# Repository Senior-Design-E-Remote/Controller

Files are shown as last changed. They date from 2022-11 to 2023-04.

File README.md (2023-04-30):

# E-Remote Quick Start Guide

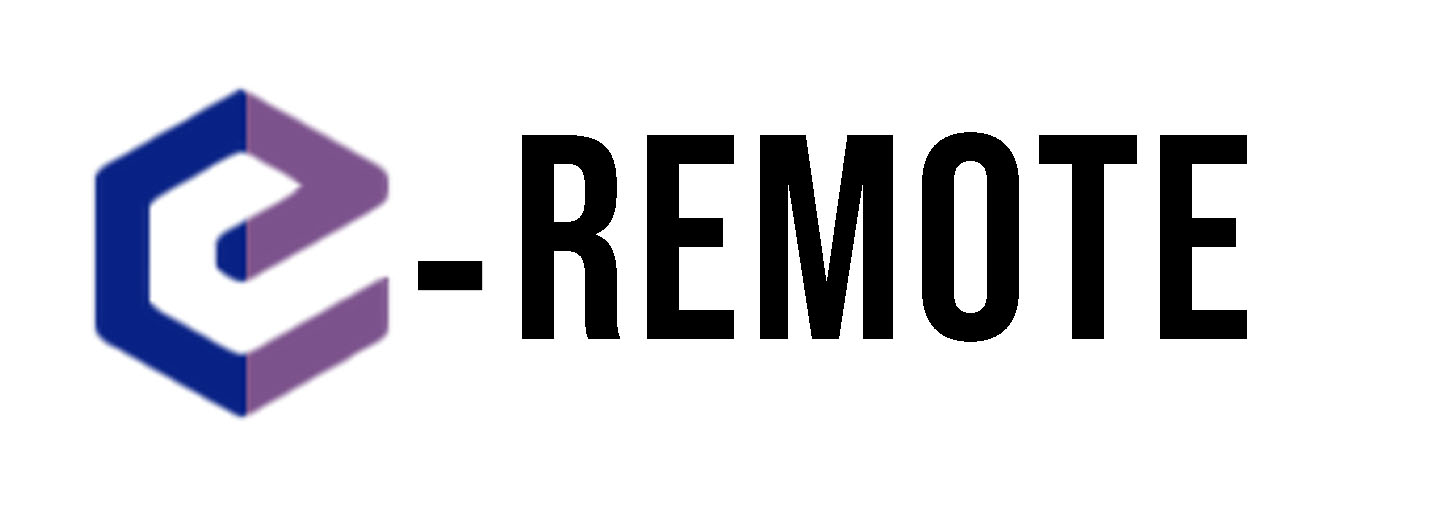
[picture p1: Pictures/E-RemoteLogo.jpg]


## Introduction and Current State

Welcome to E-Remote, an Inclusive Video Game Controller designed for people with hand arthritis. Our current product as seen below is a streamlined casing designed for maxmimm usability with minimal pain. Our finalized shell design is based on feedback from actual patients at Boston Medical Center, who's responses you can see reported in the Previous Reports folder.

Current Features include:
* Palm controlled joysticks
* Removable joystick caps with different size options available
* Touch capacitive buttons triggered by a tap
* A streamlined shell casing designed for wrist support while gaming
* Bluetooth Capabilities
* Battery and Micro USB power support
* Brightness adjustable color rotating LEDs

E-Remote is fully assembled and is currently able to connect to a Bluetooth capable computer and register itself as a generic gamepad. Once it is connected, you can open any game library that supports generic gamepads and play with minimal setup required (details for Steam can be found in the User Manual). 
On top of that, the WirelessController.ino code that powers E-Remote can also be ported to any Bluetooth capable ESP32 provided the Arduino IDE is properly setup, so you can build as many E-Remotes as you want.  

**Note**: The brightness adjusting logarithmic slider is directly connected to the 3.3V power and acts as a resistor for the LEDs to adjust their brightness. Brightness is not controlled by the code whatsoever.

### Final Product Setup

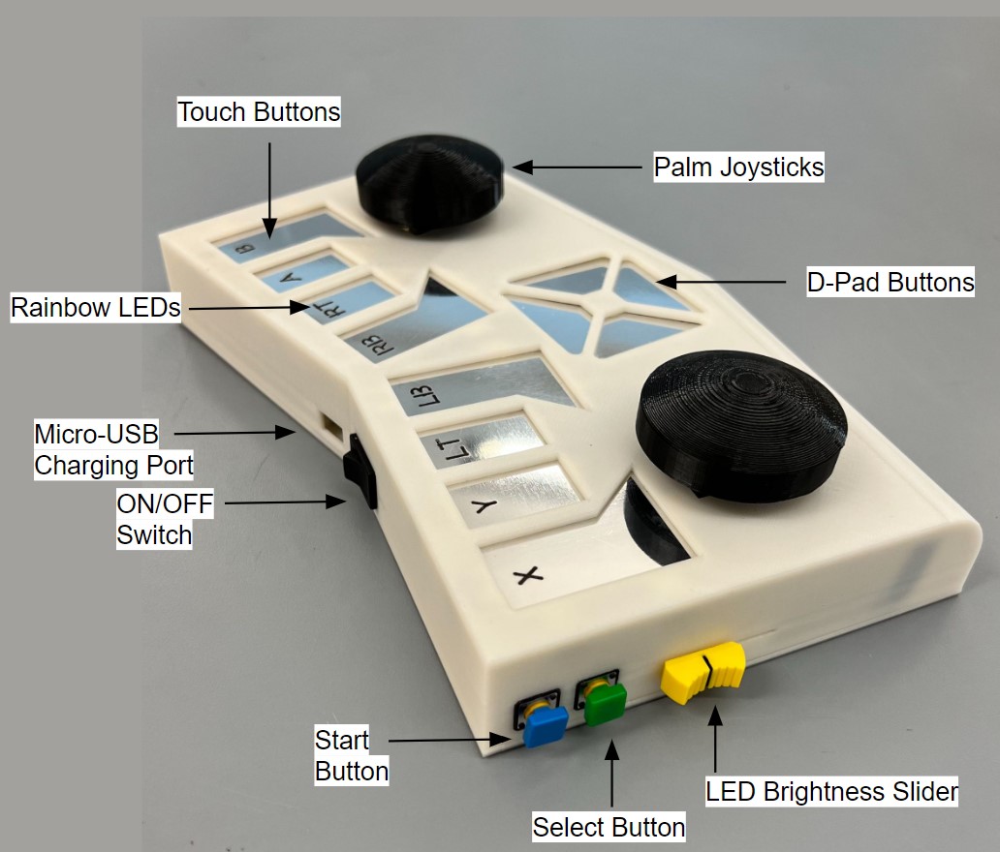
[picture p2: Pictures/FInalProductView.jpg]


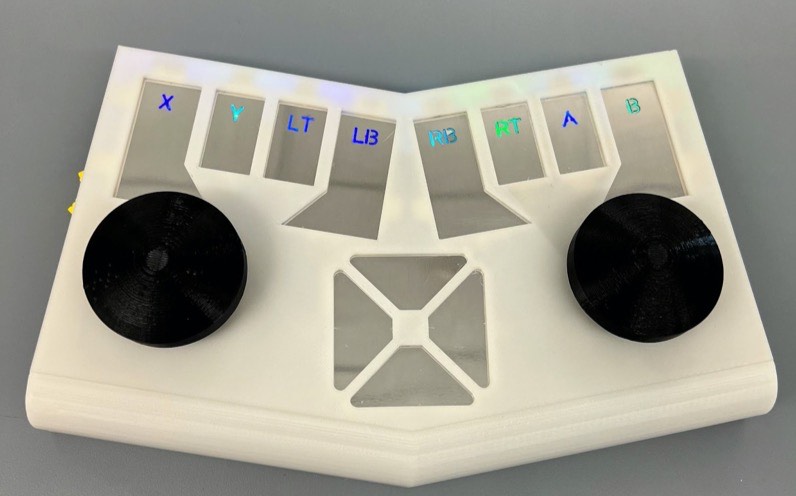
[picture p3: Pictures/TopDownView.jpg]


## Gotchas

This section is to detail any issues we encountered while developing E-Remote. Make sure to look out for these when starting your E-Remote porject.

### Software

* Some computers require the [CP210x USB to UART Bridge](https://www.silabs.com/developers/usb-to-uart-bridge-vcp-drivers?tab=downloads) driver to properly read the ESP as connected to a COM port.

* The Arduino IDE can glitch out and refuse to compile code. All you need to do is rerun the Arduino installer [here](https://www.arduino.cc/en/software) and it will fix itself.
	* All your sketches, libraries, and downloaded boards should still be there after the install.

* If the game character is slowly moving even with the joysticks at rest then there is joystick drift. Turn the device off and on again and the drift filtering code should fix it.

* if a capacitive touch button loses connection at any point during use then the device will no longer read its input. Simply restart the device and the button should work again

* If you get the "COM Port X in use" when attempting to upload in the Arduino IDE, try plugging the ESP into a different COM port or restarting your computer.

### Hardware

* The aluminum buttons do not adhere to solder. We drilled a hole to create a connection, but the connection was a bit loose. Make sure to drill small holes.

* The pre-programmed LEDs cannot be changed digitally through the ESP32 (brightness or color pattern). Slider has to be connected directly to LEDs in parallel.

* The wires that connect to the LED add enough resistance to effect the light output due to the length of the wire. Make sure all the wires connected to the LEDs’ cathode is the same length.

* ON/OFF switch could not be connected to the microcontroller because the ESP32 could not digitally turn OFF the system. Instead, the switch is connected in series with the positive side of the battery. Therefore to charge the battery, the switch has to be in the ON position.

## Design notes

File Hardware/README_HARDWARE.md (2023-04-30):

# Hardware Report

E-Remote is a wireless game controller system that utilizes an Adafruit HUZZAH32 (ESP32 Feather board) microcontroller to process user inputs and translate them into the appropriate signals for the PC to register game actions. Our system was built with the ESP32-WROOM-32E chip, enabling Bluetooth capabilities for wireless connectivity and a built-in Lithium Ion Polymer charger for added convenience.

Our hardware setup includes a rechargeable Lithium Ion Polymer battery (3.7V, 500mAh) connected to the ESP32 feather board microcontroller, which powers the system in 3.3V. An On/Off switch is also included to allow customers to easily power the controller. All electronic components are wired and soldered on a protoboard for easy assembly.

E-Remote features palm controllable joysticks with modular joystick caps in different sizes and twelve capacitive touch buttons made from aluminum sheets, which are read by an Adafruit 12-Key Capacitive Touch Sensor Breakout MPR121 chip.

We've also included Diffused 5mm Slow Fade Flashing RGB LEDs, each controlled by a corresponding capacitive touch button. The LEDs will slowly change colors, and the brightness level can be adjusted using the 10K logarithmic potentiometer slider.

Thank you for checking out the E-Remote Hardware Github repository, we hope you find our system useful for your gaming needs!

## Schematic

This schematic illustrates the electrical connections between the various components that make up the E-Remote system, including the Adafruit HUZZAH32 microcontroller, two joysticks, twelve capacitive touch buttons, one 10K ohm logarithmic potentiometer slider, and eight diffused 5mm slow fade flashing RGB LEDs

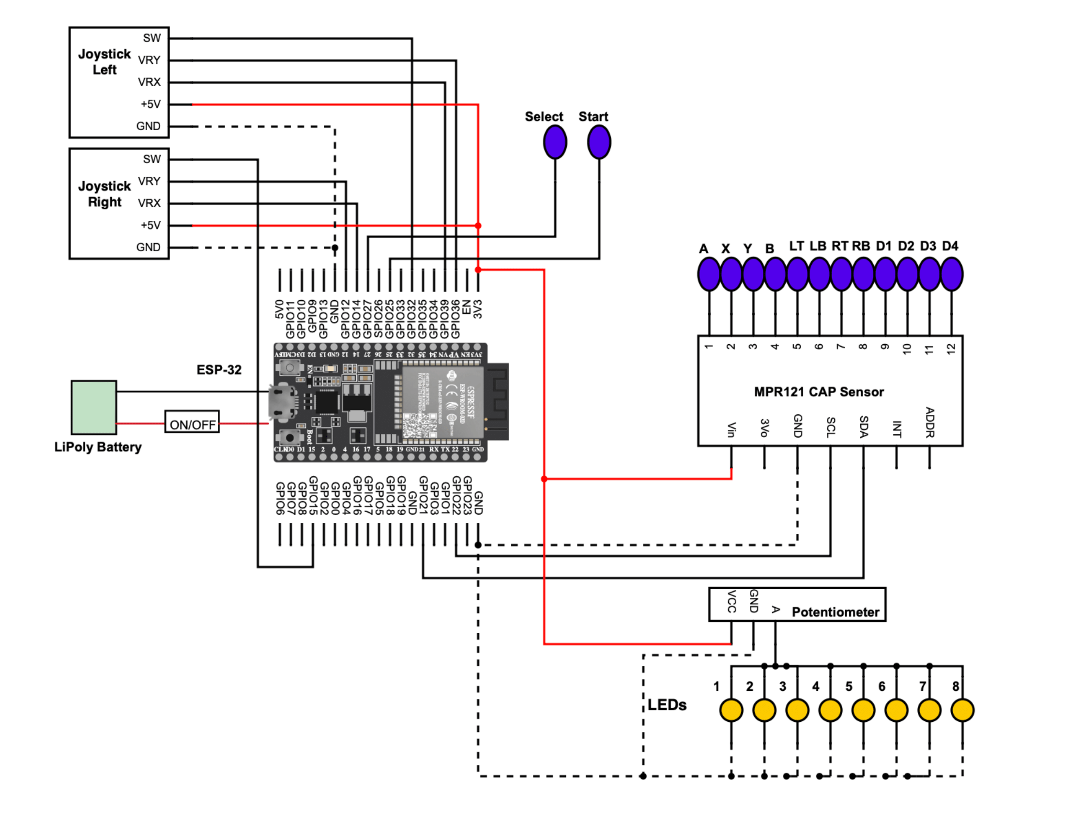
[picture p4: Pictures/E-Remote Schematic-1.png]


## Bill of Materials

The Bill of Materials provides a comprehensive inventory of the components needed for E-Remote, including their part numbers, quantities, and prices. This information can be used to source the necessary parts for building the system and to estimate the cost of the project.

| #           | Part Number | Vendor       | Bill of Materials                         | Qty | Unit Price | Total Price |
| ----------- | ----------- | ------------ | ----------------------------------------- | --- | ---------- | ----------- |
| 1           | 334382319302| eBay         | 10K Linear Potentiometer Slider           | 1   | 3.21       | 3.21        |
| 2           | 3405        | Adafruit     | HUZZAH32 - ESP32 Feather Board            | 1   | 19.95      | 19.95       |
| 3           | 1578        | Adafruit     | Lithium Ion Polymer Battery - 3.7V 500mAh | 1   | 7.95       | 7.95        |
| 4           | 679         | Adafruit     | Diffused 5mm Slow Fade Flashing RGB LED   | 8   | 0.495      | 3.96        |
| 5           | N/A         | SchlamzTech  | 2" x 6" Protoboard                        | 1   | 4.99       | 4.99        |
| 6           | N/A         | Home Depot   | 12” x 24” Plain Aluminum Sheet            | 1   | 7.31       | 7.32        |
| 7           | 1982        | Adafruit     | MPR121 - 12-Key Capacitive Touch Sensor   | 1   | 15.90      | 15.90       |
| 8           | B07PFSFFZZ  | Overture     | 3D Printer PLA Filament                   | 10  | 0.60       | 6.00        |
| 9           | 3051        | Micro Center | 22 AGW Wire                               | 4   | .07        | 0.28        |
| 10          | B01N59MK0U  | Amazon       | Joysticks                                 | 4   | 1.12       | 4.48        |
|             |             |              | **Final Total**                           |     |            | 74.03       |

## Datasheets

[HUZZAH32 - ESP32 Feather Board](https://cdn-learn.adafruit.com/downloads/pdf/adafruit-huzzah32-esp32-feather.pdf)

[Lithium Ion Polymer Battery](https://cdn-shop.adafruit.com/product-files/1578/1578+msds.pdf)

[Diffused 5mm Slow Fade Flashing RGB LED](https://www.adafruit.com/product/679)

[MPR121 - 12-Key Capacitive Touch Sensor](https://learn.adafruit.com/adafruit-mpr121-12-key-capacitive-touch-sensor-breakout-tutorial/overview)

## Power Requirements 

Voltage: 3.3V
Current: 10 mA
Power Supply Model: Lithium Ion Polymer Battery - 3.7V 500mAh

## Assembly

E-Remote is assembled by soldering all of the electronic components onto the solderable breadboard, following the hardware schematic for electrical connections. The breadboard serves as the foundation for the controller and provides a convenient platform for mounting all of the components.

As the assembly process progresses, it is important to periodically test the controller to ensure that it is functioning correctly. To check functionality, connect E-Remote to PC and see if the HUZZAH32 can be connected via bluetooth and check if the touch sensors function and LEDs turn on correctly. 

After the components have been soldered onto the solderable breadboard and tested for functionality, the next step in the assembly process is to integrate the breadboard into the 3D printed model of the E-Remote game controller. This involves gluing, taping, or inserting the components into their respective spots in the model, shown in the photos of the assembled controller below.

### Completed Circuit

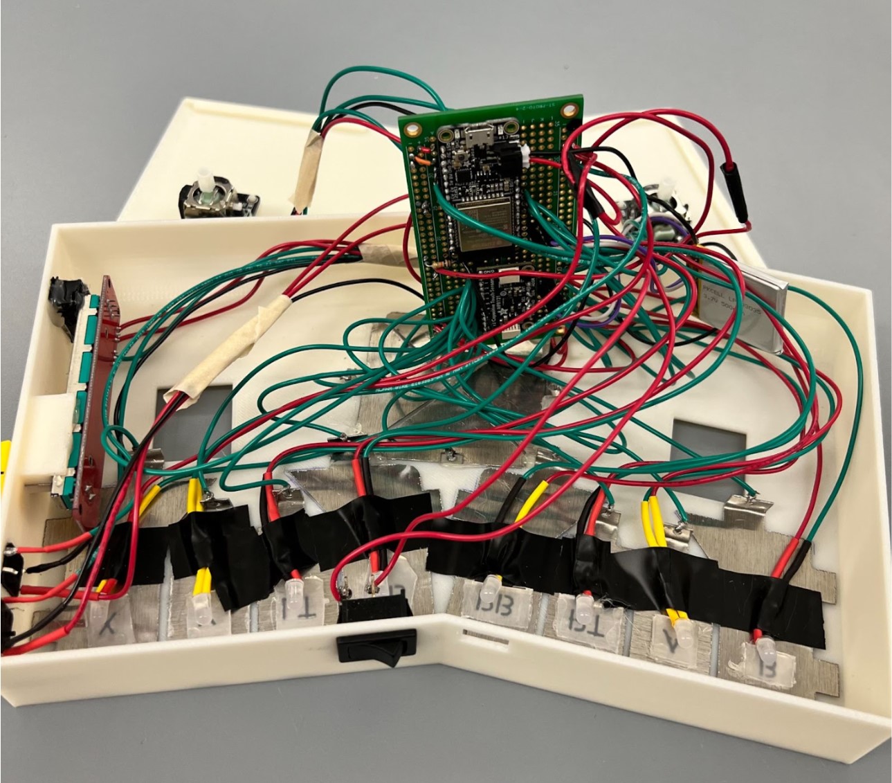
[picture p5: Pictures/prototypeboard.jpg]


### Zoomed In View

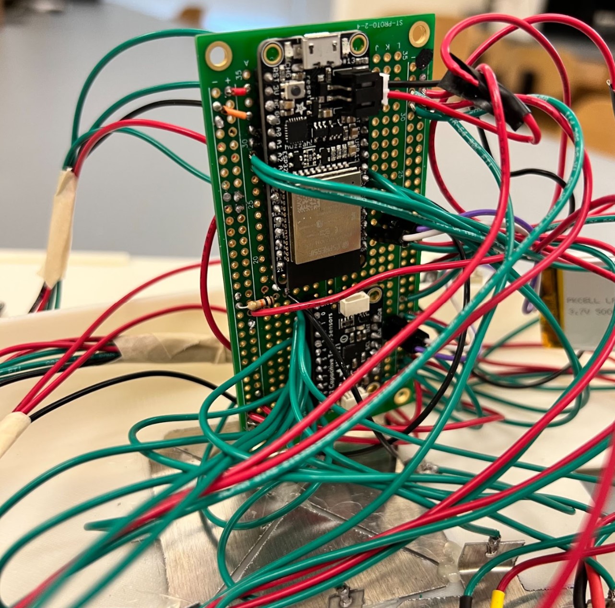
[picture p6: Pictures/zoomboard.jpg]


### Cad Visualization

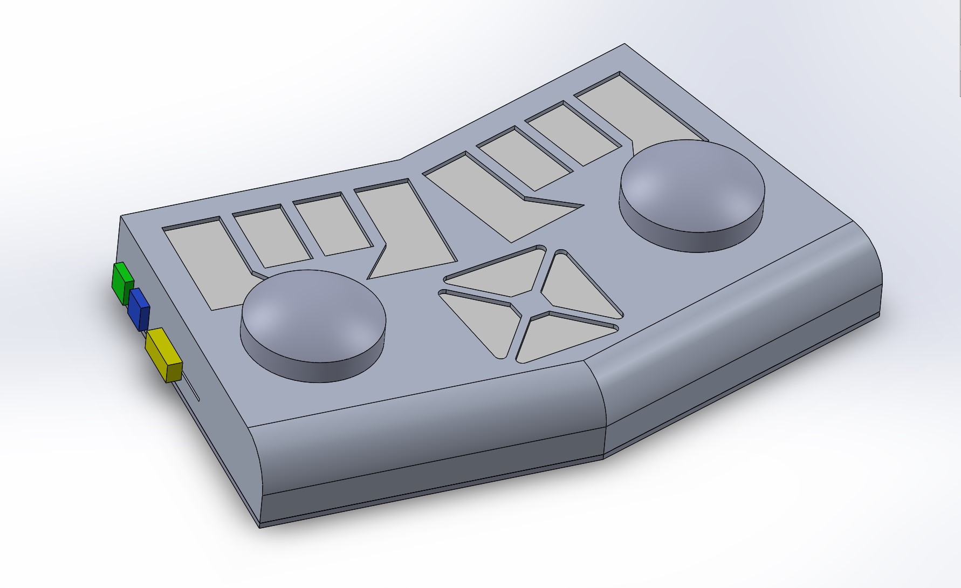
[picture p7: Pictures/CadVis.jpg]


### Assembled System



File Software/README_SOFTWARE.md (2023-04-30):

# Software Report

## Libraries

E-Remote is programmed using the Arduino IDE for its compatibility with the Adafruit HUZZAH32 ESP32 Feather board and access to the two driving libraries, Adafruit_MPR121 and ESP32-BLE-Gamepad. These two libraries are essential to the E-Remote program and implement the numerous functionalities needed for E-Remote to act as a game controller.

### Adafruit_MPR121
The Adafruit_MPR121 library is used to communicate with the MPR121 Capacitive touch board. The Adafruit_MPR121 object needs to be constructed and run its begin function, but its main use is the MPR121.touched() function which returns an uint16_t value representing the state of all twelve touch buttons. This value is then bit shifted by an amount representing the pin whose state the program wants to check and stored in a boolean value.

### ESP32-BLE-Gamepad
ESP32-BLE-Gamepad is the heart of the program as it takes the E-Remote and turns it into a video game controller. The first thing it does is enable the  ESP32-WROOM-32E chip and allow the ESP to connect to the computer via Bluetooth. Second, it registers as a Bluetooth game controller so it can be properly recognized by the computer. Finally, it takes user inputs and properly converts them to the game action signal (A button to A action, left joystick to move, etc.). 

## Wireless Controller

### Explanation
Since the ESP is programmed with the Arduino IDE, the code is written in the C++ programming language. 
The program follows the basic Arduino programming structure of the Setup and Loop blocks. 
The Setup loop is used for initialization. It declares input pins for the physical buttons, starts the MPR121 chip, and most importantly, sets the configurations for the ESP32-BLE-Gamepad so there are no extraneous controls added.
The Loop will cycle through every user input and check its current state, and send its corresponding signal to the computer. 

If the input is a button (physical or touch), the program will check its current state against its previous state and will only send an updated signal if the state has changed, preventing extraneous repeat signals from being sent. 
It is important to note that although the state storage arrays and library variables are global variables, this is normal for Arduino-style code since there is no singular Main function to both declare and use variables and the loop and set-up blocks cannot access each other's variables. 

The joysticks are not as simple as they output noise when at rest which can cause the player controlled character to move even when their hands are at rest. 
To circumvent this, the device will take 3000 reads from each joystick axis and finds all their maximum and minimum values. Then, while in the loop, the code will take 100 reads of each axis and average them to find a value. 
If this value falls inside of the max and min for that axis, the code will instead send a rest value of 16383 which is true neutral for any joystick axis. 
Otherwise, it will map the value from the joysticks 0-4095 to the computer's range of 0-32767 to find the movement position.

### Pseudocode

```
Setup {
    MPR121 Begin
    Physical Button Pins = Input
    Set Gamepad Configurations

    for each Joystick Axis{
        Take 3000 reads
        Set Axis Max
        Set Axis Min
    }
}

Loop {
    Poll Inputs

    If Button{
        Check previous state and send Button Signal if changed
    }
	
    If Joystick{
        Average 100 reads
        If Average in Rest Range: send Rest Val
        Else: Map 0-4095 -> 0-32767
    }
    Send Joystick Signal
}
```

### Block Diagram

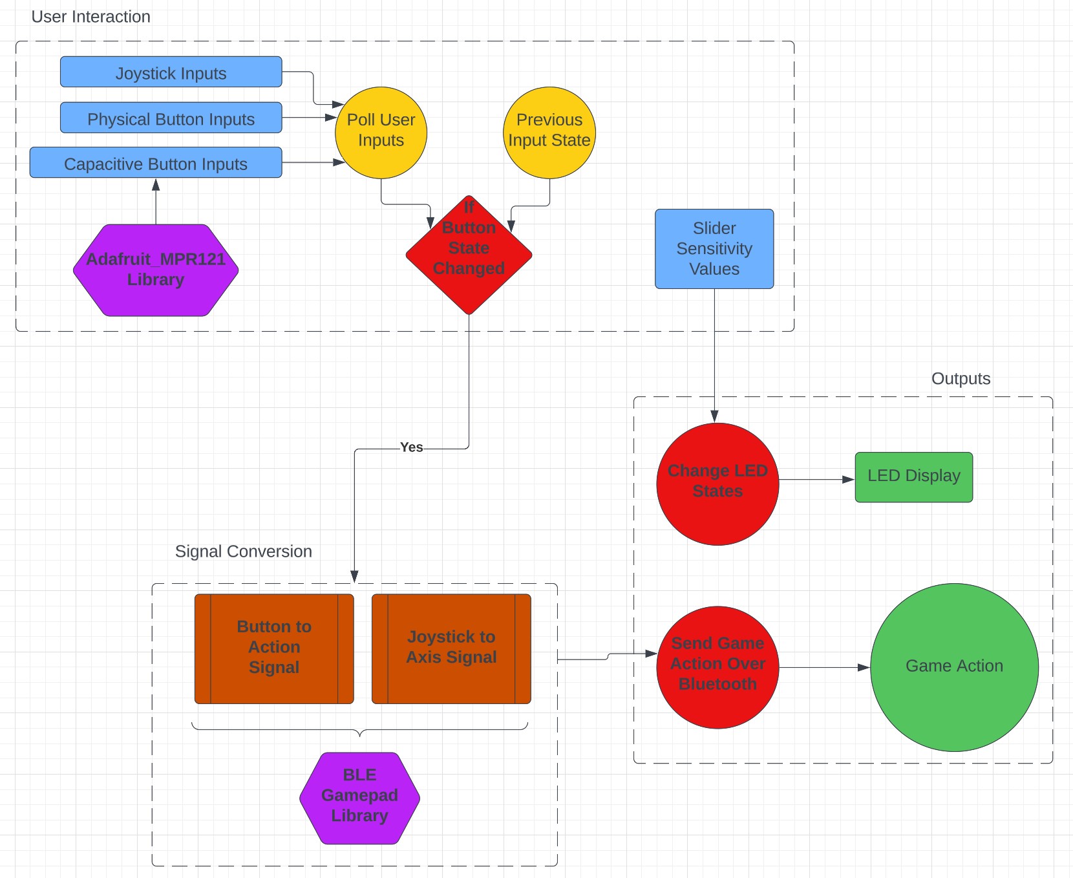
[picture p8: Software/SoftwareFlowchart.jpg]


## Using the Code
### Setup
In order to upload the WirelessController code to your ESP, you need to setup the Arduino IDE, which you can install [here](https://www.arduino.cc/en/software).

#### Step 1: Installing the Boards
The Arduino IDE does not come with the ESP boards preinstalled, so you need to follow a few simple steps in order to get them installed. 

1. Go to **File** -> **Preferences** to open the preferences menu. 

2. Copy this url: https://raw.githubusercontent.com/espressif/arduino-esp32/gh-pages/package_esp32_index.json to the text box labeled "Additional Board Manager URLs". 

3. Go to the Board Manager and search for esp, they should pop up and you should be able to hit install. Wait for the install to finish and you should be able to select ESP boards.

#### Step 2: Installing the Libraries
There are two different methods of installing the required libraries depending on what version of the Arduino IDE you have. 

1. Go to the Libraries Manager and search for both the Adafruit_MPR121 and ESP32-BLE-Gamepad libraries. Both should come up and there will be an option to install both.

2. If th libraries do not automatically appear in the Libraries Manager, go to the Githubs for each library found [here](*https://github.com/adafruit/Adafruit_MPR121) and [here](https://github.com/lemmingDev/ESP32-BLE-Gamepad). Download them as zip files, go to **Sketch** -> **Include Library** -> **Add .Zip Library**, and select the zip files. The library should appear in the library manager where you can then install them.

### Uploading the Code:
Now that the Arduino IDE is properly configured, you can now upload the code to your ESP by following these steps.
1. Plug your ESP into the computer 
2. Open the Arduino IDE and open the Board Manager
3. Choose the Adafruit ESP32 Feather as the board for the corresponding COM Port.
    * **Important Note**: Some computers require the [CP210x USB to UART Bridge](https://www.silabs.com/developers/usb-to-uart-bridge-vcp-drivers?tab=downloads) driver to properly read the ESP as connected to a COM port.
4. If the text in the Board Manager dropdown menu becomes bolded, that means the ESP is connected and you can begin the upload.
5. Wait for the upload to finish and verify the code is working by going to your bluetooth menu and see if E-Remote is available to connect
    * Note that first time compiling and uploading can take upwards of 5-10 minutes as the ESP32-BLE-Gamepad library takes a long time to compile. This will go down in subsequent compilations.

If all is successful, you can connect to E-Remote through your computer's bluetooth menu where it will be registered as a generic gamepad. You can then connect it to the game library of your choice (we used Steam and you can find those steps in the User Manual).

## Other Code
This section will explain the other code found in the Software folder of this repository. These are various examples of hardware and other controller code that we made to help develop the final E-Remote product
### Hardware Examples
In this folder are various examples we made to test hardware for the E-Remote. These include tests for the logarithmic slider, a test for joystick drift, and several examples of tests for the MPR121 and the capacitive touch buttons. These examples should help you test individual hardware should you run into trouble with any of your components.
### Wired Controller
In this folder is the code for a wired controller which was the first working version of our controller code. This code is only compatible with the [Arduino Micro](https://store.arduino.cc/products/arduino-micro) and the [Arduino Leonardo](https://store.arduino.cc/products/arduino-leonardo-with-headers?queryID=undefined) as they are the only board with the ATmega32u4 which allows for USb communication with a computer. This example uses the XInput library and is a similar concept to the wireless controller code, but without the need to check previous button state or filter analog joystick noise as the library handles it automatically. When connected to a computer, it automatically registers as an Xbox 360 controller and works as any other Xbox controller would. This is an interesting tradeoff with the E-remote as the Wired controller has an easier setup with the predefined Xbox controls but loses the user customizable controls that come with E-Remote's generic gamepad status. 

Note: if you wish to run this code, the XInput library requires its own version of board installs. Just input follow Step 1 in the Setup section and use this url: https://raw.githubusercontent.com/dmadison/ArduinoXInput_Boards/master/package_dmadison_xinput_index.json

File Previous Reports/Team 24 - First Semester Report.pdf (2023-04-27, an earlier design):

EC463 - BOSTON UNIVERSITY ELECTRICAL & COMPUTER ENGINEERING CAPSTONE SENIOR DESIGN PROJECT | 1

# E-Remote: Inclusive Video Game Controller

Team 24: Seok Young Choi, Nicholas Gutierrez, Eunhye Kwon, and Yumin L. Wei

Executive Summary (Lisa and Eunhye)— With the growth of the internet, human connection is not only limited to those physically present. Online communities are growing and the gaming community is an example of an upcoming space for people from all over the world to meet. But joining a gaming community is not as easy as switching the on button. The barriers of entry still exist in this new social platform, especially for those with disabilities. Other companies have tried to create inclusive video game controllers to lower these barriers, but those controllers come with their own problems as well. The final deliverable of our project is to have a working video game controller compatible with PC through Bluetooth connectivity. The controller should have full functionality with at least four different genres of video games: arcade, puzzle, racing, and shooting. The user should play with minimal to no pain reported after 30 minutes. We will also provide a programmed Arduino Micro that handles inputs from the controller buttons and sends the proper signal over Bluetooth to the PC and a user manual that details the operation of the controller and how to easily connect it to a PC. Our product, E-Remote, will have innovative features such as palm-controllable joysticks, touch sensor buttons, and Bluetooth connectivity. These features will eliminate problems of conventional video game controllers and provide a fun and comfortable gaming experience for individuals with rheumatoid arthritis.

Index Terms—Channels and controllers, Combinational logic, Data communication devices, Portable devices, Real-time and embedded systems, Wireless systems
—————————— u ——————————

### 1 INTRODUCTION (LISA )

in the last few years, it seems like more people than ever have realized the importance of being able to share experiences online. One of the most popular ways to connect with others online is video games. Unfortunately, the handheld controllers required for most games can act as a barrier to entry for those with physical disabilities. Individuals with rheumatoid arthritis form 14% of the disabled gaming community and have reported to face problems using modern controllers for PlayStation, Xbox, etc. that require the player to have a high level of dexterity [1]. To increase accessibility of playing video games, we propose an inclusive video game controller designed to fit the needs of individuals with rheumatoid arthritis. Our product, the E-Remote will be able to provide a fun and intuitive gaming experience for individuals with rheumatoid arthritis. The E-Remote is an inclusive video game controller, rated E for everyone!
Within the ever-growing gaming community, 20.5% of that population are individuals with disabilities [1]. In Fig. 1, researchers ask disabled and non-disabled gamers, “In the last 12 months have you purchased any in-game add-ons or subscriptions?” It was found that those with disabilities are reported to be more engaged with purchasing adjacent gaming content, such as add-ons, Twitch streams, Reddit posts, etc. [2]. With such a large community of actively engaging consumers, it is a disservice when companies are slow to create inclusive video games, and even slower to create specialized controllers.

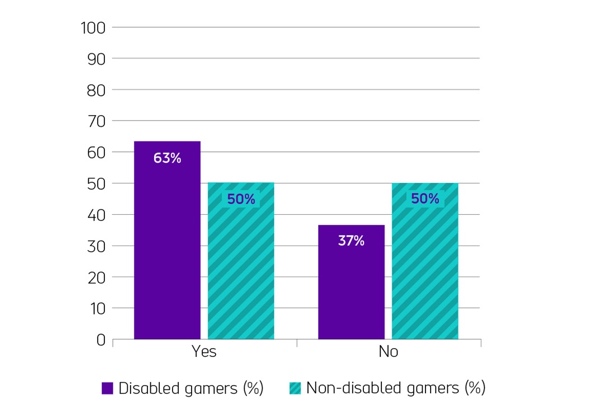
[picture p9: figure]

The most common physical disability that gamers face is rheumatoid arthritis, standing at 14% of the disabled gaming community. Rheumatoid arthritis (RA) is “a chronic inflammatory disorder affecting many joints, including those in the hands and feet” [3]. Studies have shown that for people with RA, gaming allows the player to take their mind off of their chronic pain, but extended use is painful [4]. In an interview with a RA patient, they criticized many problems with the standard controllers and even some inclusive controllers that already exist. The main problem is that people with RA cannot hold a flexed hand position for a long time, especially when holding something too heavy and rigid.

Boston University Electrical & Computer Engineering Capstone Senior Design Project

I

Fig. 1. Bar graph showing the survey results of “In the last 12 months have you purchased any in-game add-ons or subscriptions?” [2]

————————————————
- Seok Young Choi is with the Department of Electrical and Computer Engineering, Boston University, Boston, MA 02215. E-mail: schoi11@bu.edu
- Nicholas Gutierrez is with the Department of Electrical and Computer Engineering, Boston University, Boston, MA 02215. E-mail: ng0805@bu.edu
- Eunhye Kwon is with the Department of Electrical and Computer Engineering, Boston University, Boston, MA 02215. E-mail: ekwon23@bu.edu
- Yumin L. Wei is with the Department of Electrical and Computer Engineering, Boston University, Boston, MA 02215. E-mail: ylisawei@bu.edu

2 | EC463 - BOSTON UNIVERSITY ELECTRICAL & COMPUTER ENGINEERING CAPSTONE SENIOR DESIGN PROJECT

Small and intricate movements, such as pushing buttons that are close together, cause unnecessary pain.
E-Remote will address these issues with current controllers by creating a prototype of a portable inclusive video game controller, along with all the embedded hardware, specialized for customers with rheumatoid arthritis. It should be compatible with at least a PC and four popular video games in the market. Lastly, it should create a unique and fun gaming experience for each gamer.
The main problems that they face at the moment include heavy weight, uncomfortable buttons, painful repetitive motions, a steep learning curve, and a high price point. All of these problems can be seen in Fig. 2, where the largest barriers faced were affordability, knowledge or time to set up and technology. In contrast, our design will be an inclusive video game controller that will allow users to forgo these problems and play games effortlessly. To eliminate the weight problem, the product will rest on a flat surface, therefore, allowing a longer playtime. Significant features of our product are the palm-controllable joysticks and touch sensor buttons. We would replace the standard buttons with lightup, touch-sensor buttons. The joystick will also be replaced with a ball-in-socket component allowing a relaxed hand position. The design should also be intuitive, allowing the player to fully understand the controller after five minutes of use. The price point we are aiming for is less than $99.99 which is the cheapest price on the market right now [5]. These are all the features that we hope to include in our final project in order to make the gaming community a little more accessible.

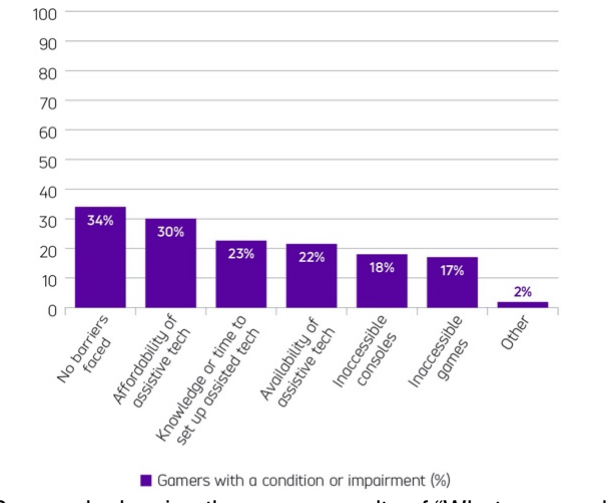
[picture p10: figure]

### 2 CONCEPT DEVELOPMENT (SEOK YOUNG)

The overall goal of the design process is to minimize the movement of hands and fingers while using the controller and allow users to be able to control the device effortlessly because people with RA are having pain coming from making elaborated motions. In addition to avoiding the shape that should be held with both hands, an interviewer mentioned that they most feel comfortable and have less pain when they are resting their hand and arm, just like naturally putting them on a table. Hence the controller is designed to be used while placed on a horizontal platform, having buttons and joysticks on the same plane of the controller so that the user is not necessarily moving or reaching their hand far away but a simple movement during the game.

### 2.1 Joysticks

The controller is mainly constructed with two palm-controllable joysticks, and they are linked to the rectangular casing where both hands can be placed on the top. Basic mechanism of the palm joystick is identical to the conventional joystick using the ball-and-socket joints which enable movement and rotation to all directions. Our joystick design has a wider and bigger surface area that can be controlled easily without applying forces or moving a certain part of the arm frequently. Final shape of the controller resembles the pancake, which has a low profile and smooth slope angle so that it could fit a wide range of shape and size of hands. As shown in the Fig. 3, each joystick has a diameter of 3.36 inch and height of 0.88 inch including 0.30 inch of a vertical bottom edge to provide a grip for users if needed.

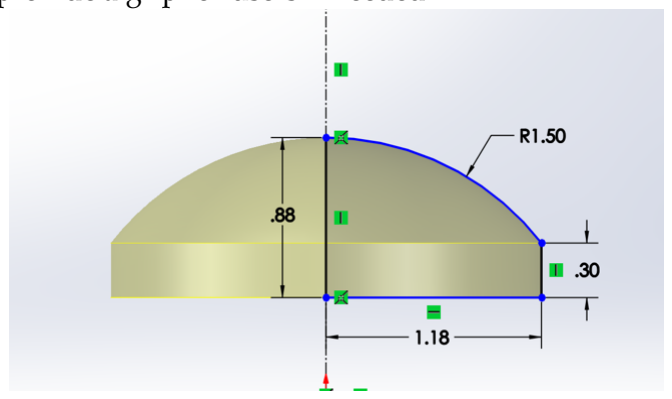
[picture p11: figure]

One of the initial ideas was the roller ball joysticks that are implemented inside of the casing, and detecting the movement of the joystick by gyroscope sensors which are placed inside of the spheres. This method might aesthetically be a better option; however, it has limitations that will exceed the price because of its complex mechanism, compatibility with the microcontroller, and most importantly, this design requires players to use their wrist to control the joystick, which is not ideal for people with RA.

Fig. 3. Sketch of the joystick with dimensions

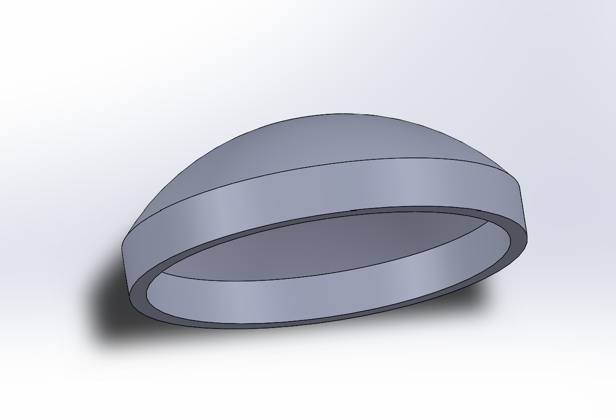
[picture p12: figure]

Fig. 4. 3D modeling of the joystick

Fig. 2. Bar graph showing the survey results of “What poses a barrier or issue to gaming for you?” [2]

E-REMOTE : INCLUSIVE VIDEO GAME CONTROLLER | 3

### 2.2 Buttons

Total of eight buttons are located on the upper side of
the joystick, which can be easily reachable with four fingers - index, middle, ring, and little fingers - when controlling joysticks with palms. The most important specification for the buttons is that it has to be pressed easily and effortlessly to avoid applying significant force. Rather than implementing physical, push down buttons, capacitive touch sensors were used which detects a change in capacitance on an area so that even a small amount of touch or contact will make an input [6].

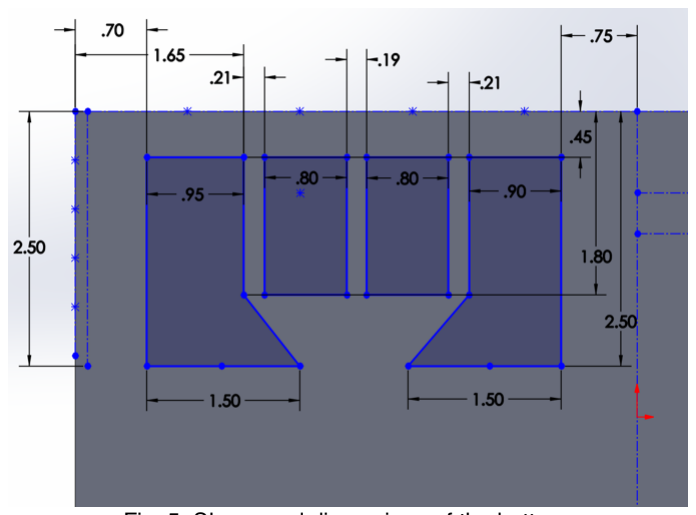
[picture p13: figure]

### 2.3 Convenience Features

The controller has convenience features that will allow users to have a better experience while using the product. To enhance visibility while playing games, LED lights are mounted around the buttons. LEDs are initiated as user inputs and gradually diminished in a second. Brightness can be adjusted using one of the slider knobs on the side of the controller, and the other slider is for changing the sensitivity of the capacitive touch sensors.
As the controller is designed to be placed and used on a surface, detachable base filters are included, and possible material options are memory foam, suction cups, rubber, and velcro.

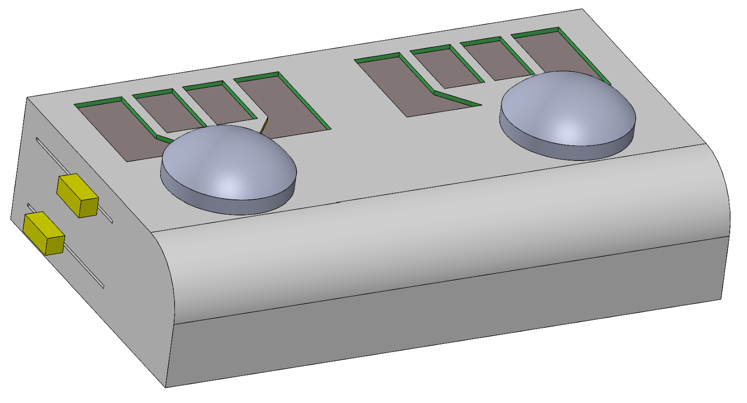
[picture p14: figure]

The edge of the casing that faces the users is smoothed for wrist support; soft padding is provided for users who play games for a long time. On top of the wireless Bluetooth connectivity, a case that covers the upper part of the controller will also be provided for increased durability and protection of the device. Fig. 6 shows a visualization of final packaging of E-Remote and the current prototype we have is in Appendix 4.

### 3 SYSTEM DESCRIPTION (NICK)

### 3.1 Hardware

The hardware for the system is powered by four 1.5V Rechargeable Batteries which are connected to a TP4056 Lithium battery charging board. The charging board is wired to an on/off switch which can be used by the customer to power the controller. The controller itself is driven by several inputs and outputs taken from the user and the PC. The first set of inputs is two joysticks, each with a 5V input pin, a ground input pin, an X-axis analog output, a Y-axis analog output, and an SW push button digital output that allows the user to press down on the joystick and send a button input.
Next, the controller uses the Adafruit 12-Key Capacitive Touch Sensor Breakout MPR121 chip to read inputs from eight capacitive touch buttons made from copper sheets. These touch sensors remove the need to press a button, as they send a high signal when tapped. The final inputs are two 10K logarithmic potentiometer sliders used to adjust the sensitivity of the capacitive touch buttons and LED brightness.
Outputs from the controller consist of eight LEDs, each one controlled by a corresponding capacitive touch button, and the game action signals are mapped from the user inputs. The system is controlled by an ESP32-DevKitC-32E microcontroller which takes in all user inputs and translates them into the correct signals needed by the PC to register a game action. The ESP32-Dev-KitC-32E was chosen for its embedded ESP32-WROOM-32E chip which allows for Bluetooth capabilities and allows our controller to wirelessly connect to any PC with Bluetooth support.

### 3.2 Software

The Arduino IDE is used to write the software for the controller and uses the standard Arduino setup and loop structures as the foundation for the program (Note that ESP32 is compatible with the Arduino program structure). Upon startup, the program will declare and initialize all I/O pins required by the LEDs, sliders, and joysticks. Next, it will verify that the Capacitive Touch Sensor Breakout has been connected. If the chip is not connected, then the program will turn on the Onboard LED and loop until the chip is connected.
After the setup section is completed, the program enters the loop section which will continue until the device is powered off. In the loop, the microcontroller will read the current state of every input device and determine if the state has changed since the last poll. If there is a change in state, the program will send a new signal to the PC indicating the change in in-game action and change the state of the corresponding LED. The program will also detect any changes in the slider

Fig. 5. Shape and dimensions of the buttons

Fig. 6. Visualization of E-Remote Casing

4 | EC463 - BOSTON UNIVERSITY ELECTRICAL & COMPUTER ENGINEERING CAPSTONE SENIOR DESIGN PROJECT

values and adjust the sensitivity of the LEDs/touch
buttons which should take effect in the next loop. The
average input lag from user input to an in-game action
being performed should be less than 15 ms. The following is high-level pseudocode of how the controller will operate.

### 3.3 System Diagram

The system diagram (Fig. 7) illustrates the flow of the system once powered on. The ESP reads slider values, polls the user inputs, and then determines if there is a change in state for any input. It then changes any LED states that had their corresponding input state changed and prepares to send the game action signal. Before sending the new signals, the ESP needs to translate the input states to the correct Bluetooth signals that can be properly identified by the PC. Finally, the PC receives the new set of signals and completes game actions accordingly.

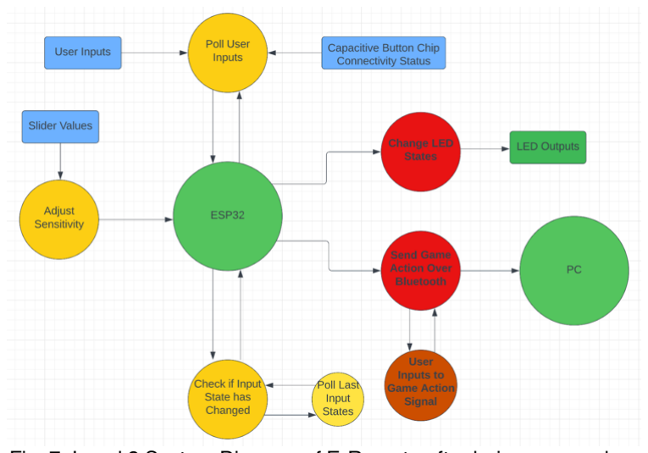
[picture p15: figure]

### 4 FIRST SEMESTER PROGRESS (LISA)

The first action we took was researching the inclusive video game market and audience to brainstorm designs that solved the specific problems we found. To investigate these problems, we researched a casual gamer with RA. After the interview, we created an ergonomic design that solved the physical problems mentioned before. We took that drawing and turned it into a 3D model on solid works and printed the first iteration. Since it was the first print, we revised the sizes and distances of the buttons. The specific adjustments can be seen in Appendix 5.
Since that first print, we have printed two more revisions, changing the buttons and adding sections for specific electronic parts.
In parallel, we also focused on the hardware portion of this project. Starting by making a hardware block diagram (seen in Fig. 8), we mapped out all the electronic components necessary for each section of the block diagram. From there, we order some of the electronic components to start testing: Arduino Micro, tactile buttons, joysticks, potentiometer sliders, and LEDs.

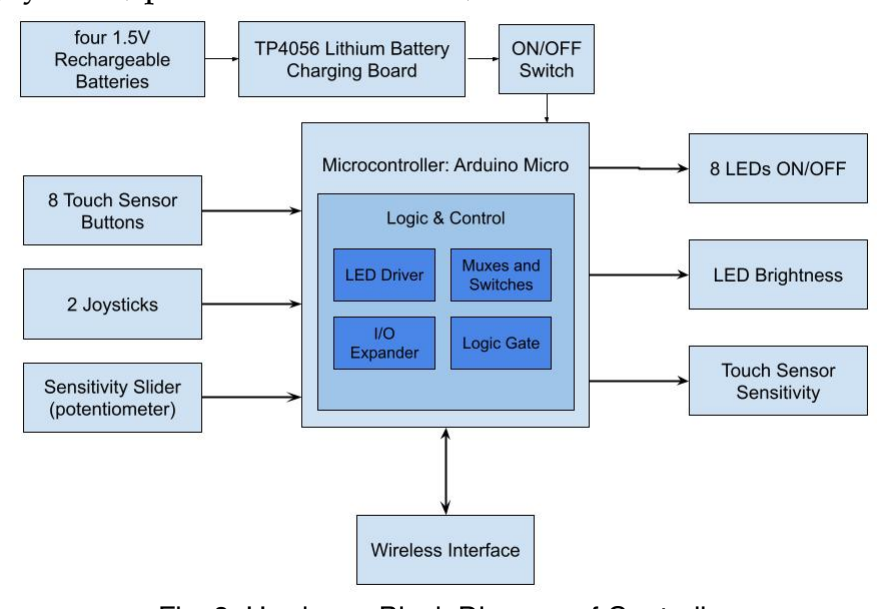
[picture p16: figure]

Using these parts, we started to build the circuit in sections. First were eight tactile buttons, eight LEDs, and an Arduino. We wrote a simple code that turned on the LED once the corresponding button was pressed. They replaced the eight tactile buttons with a touch capacitive board with eight touch buttons. In order to understand the touch capacitive board, we tested different materials and their compatibility with the board. These tests can be seen in Appendix 6. The purpose of this test was to determine the material(s) that could be used as touch sensor pads for E-Remote.
At the moment, we have a working breadboard controller with eight touch buttons, eight LEDs, two joysticks, and an Arduino Micro. The schematic of these components can be seen in Appendix 7.
We also worked extensively with the software necessary for this project. We started by creating a software flow diagram in order to map out the logic of the code. As you can see in Appendix 8, the block diagram loops through each input to make sure there is not a state change; if there is a change in state, the output will then be activated.
Next, we used the Arduino library to write a code that reads inputs from push buttons and maps them to controller inputs which are then sent over USB to the computer. The code can also read push button inputs and turns on/off the corresponding LED. In order to test the system, we wrote a testing procedure to confirm the functionality of these inputs and outputs. Appendix 9 shows the functionality of buttons and joysticks will be tested through LED outputs, gaming controller

Fig. 7. Level 2 System Diagram of E-Remote after being powered on

Setup {
Assign I/O
Initialize I/O
while (CapacitiveButtonChip Not Connected) { Start Onboard LED
}
Stop Onboard LED
}

Loop {
For (Input in Inputs) {
If (Input Has Changed) {
Send new game action signal to PC Set Outputs (Input)
}
}

Fig. 8. Hardware Block Diagram of Controller outputs, and game action performances. From our tests, the system was working well.

### 5 TECHNICAL PLAN (EUNHYE)

We have made substantial progress in our current prototype but there are still more tasks to be done to complete our proposed solution of an inclusive video game controller. To complete this project, the next steps will be divided into three phases: hardware requirements, integration and test, and finalization. A Gantt chart summarizing the project schedule from December 11, 2022, to May 1, 2023, is in Appendix 2. The following sections will discuss specific tasks to be completed in each phase.

### 5.1 Phase I: Hardware Requirements

Task 1: Potentiometer
Two 10K logarithmic potentiometer sliders shall be implemented within the circuit architecture and tested. They shall have an operating region of 3.3 - 5V and output a range of 0 - 5V. The resulting output depends on the slider's location. Each potentiometer slider shall utilize one analog pin on the Arduino Micro and control LED brightness or touch sensor sensitivity. The circuit should be tested with a dummy voltage of 4V. Lead: Eunhye, Assisting: Lisa.
Task 2: Touch Sensor Design
Eight touch sensor pads shall be designed, fabricated, and tested. It shall be made with conductive material, such as aluminum, have laser-cut holes for LED light to shine through, and be covered by clear conductive material. The touch sensor pads shall be connected to the MPR121 capacitive touch sensor breakout board by soldered wires. The design should be tested by MPR121 touch sensor input signals and LED light visibility. Lead: Seok Young; Assisting: Lisa.
Task 3: LED Lighting Design
Eight LED lights of different colors shall be designed and implemented in touch sensor architecture. They shall be compact and placed under the touch sensor pads and implemented in the circuit to turn on/off based on touch sensor input. Lead: Seok Young; Assisting: Eunhye, Lisa.
Task 4: Rechargeable Battery Supply
Four 1.5V rechargeable batteries connected to a 5V, 1A MakerFocus TP4056 Lithium Battery Charging Board shall be implemented within the circuit architecture and tested. It shall be rechargeable and meet specifications for weight, battery life, and heat dissipation. The rechargeable battery should be tested with a dummy load of 500 ohms. Lead: Lisa; Assisting: Eunhye.
Task 5: Bluetooth Connectivity

A microcontroller with Bluetooth capabilities shall replace the Arduino Micro in the current circuit architecture. The ESP31-DevKitC-32E microcontroller with embedded ESP32-WROOM-32E chip which allows
Bluetooth | capabilities | shall | provide | wireless
connectivity to any PC and control the video game controller system. All electronic components such as joystick modules, a capacitive touch sensor breakout module, LED lights, and rechargeable batteries shall be
transferred | onto | the | ESP31-DevKitC-32E
microcontroller. The design shall be tested by 30 minutes of gameplay via Bluetooth connection to a PC and input lag calculations. Lead: Nick.

### 5.2 Phase II: Integration and Test

Task 6: Solder Breadboard Design
A solder breadboard shall be designed, fabricated, and tested. It shall have all electronic components and wires soldered onto the breadboard for proper circuit connections and meet specifications for weight and durability. It shall be tested for all electronic components, connections, and I/O ports. Lead: Lisa; Assisting: Eunhye. Task 7: Final Software Design
The final software of the controller system shall be developed and tested. It shall connect all electronic components of the controller and send information to the PC. It should be tested that the average input lag from user input to an in-game action being performed is less than 15 ms. Lead: Nick.
Task 8: Packaging Design I
An initial controller packaging shall be designed, fabricated, and tested. The 3D printed controller packaging shall hold all electronic components such as breadboard, joystick, buttons, LEDs, and batteries, and meet all specifications for dimensions, weight, and cost. The controller packaging should be tested for comfort and durability by clients with rheumatoid arthritis. Lead: Seok Young.
Task 9: Client Testing and Feedback
A group of clients with rheumatoid arthritis shall test and provide feedback on the first packaging design. The group size shall be 10 - 20 individuals with rheumatoid arthritis and they shall complete a survey and provide feedback on the user interface and overall usability of the product. The feedback from clients should be used to revise the packaging design. Lead: Eunhye; Assisting: Lisa.

### 5.3 Finalization

Task 10: Final Prototype Test
All electronic components and software shall be implemented in controller packaging and tested. They should be tested for input lag and 30 minutes of gameplay of four different game genres. The prototype shall meet all specifications for requirements and functions. Lead: Lisa, Nick; Assisting: Eunhye.
Task 11: Final Packaging Design

6 | EC463 - BOSTON UNIVERSITY ELECTRICAL & COMPUTER ENGINEERING CAPSTONE SENIOR DESIGN PROJECT

Final packaging of the controller shall be designed, fabricated, and tested. The packaging shall be revised from
the first design following feedback from clients. The 3Dprinted packaging shall hold all electronic components, eight touch sensor buttons and lighting, two palm joysticks, and detachable bases. The packaging shall be tested for functionality and durability by carrying it around in a backpack for a day. Lead: Seok Young. All of these tasks will help complete our proposed solution by the week of April 1, 2023, for the functional testing of the product. The month of April 2023 will be dedicated to product revision (if needed), customer installation, and preparation of the final report due by the end of April 2023 and ECE Day on May 5, 2023.

### 6 BUDGET ESTIMATE (LISA)

The most expensive component so far is the Arduino Micro which was $55.24 for two. In addition, we bought four Touch Capacitive Boards for $60.65 because we accidentally made soldering errors with the first batch we bought. Besides those big purchases, the majority of our materials have been donated by members through past projects or from the Boston University ECE department. Table 1 includes the list of items used so far.

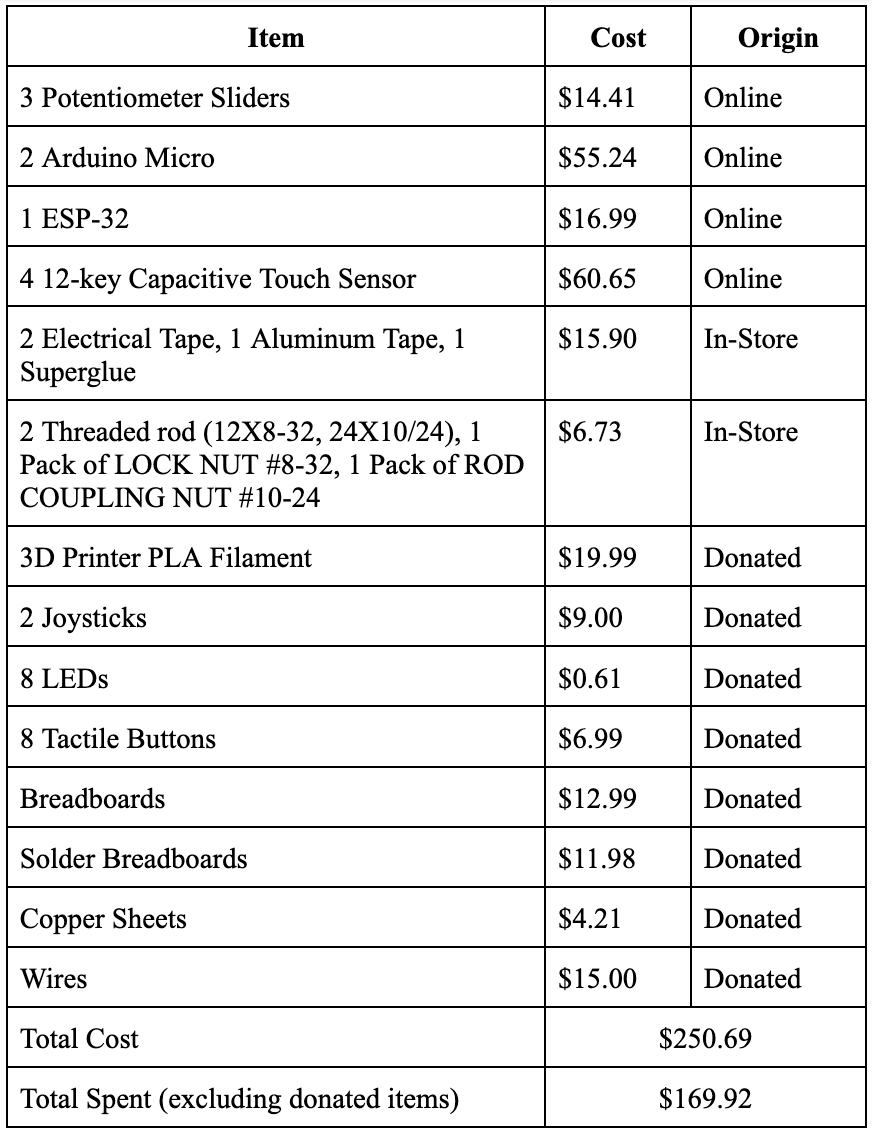
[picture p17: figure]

Table 1. Total Budget Estimated (Last Updated: 12/9/22)

### 7 ATTACHMENTS

### 7.1 Appendix 1 - Engineering Requirements (Seok Young)

Team # 24 | Team Name: E-Remote: Inclusive Video Game Controller
Project Name: Inclusive video game controller
Requirement | Value, range, tolerance, units
Case dimensions | 11 inch × 6 inch × 2.5 inch
Joystick dimensions | ⌀ 3.36 inch (diameter) × 0.88 inch (height)
Buttons | User programmable capacitive touch sensors
Input lag | < 15 ms
Power | Rechargeable 3.3V lithium-ion batteries 24-hour runtime / charge
Bluetooth sync time | < 30 secs
Connection range | < 10 m (33 ft)
Weight | < 1.33 lbs
Constraints | Able to carry, fit in a 22 inch × 14 inch × 9 inch size backpack
Cost | < $99.99

### 7.2 Appendix 2 - Gantt Chart (Eunhye)

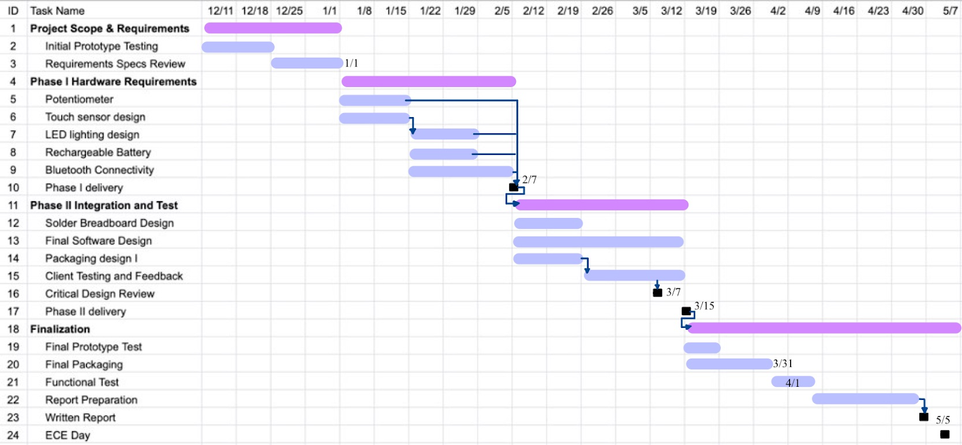
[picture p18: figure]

8 | EC463 - BOSTON UNIVERSITY ELECTRICAL & COMPUTER ENGINEERING CAPSTONE SENIOR DESIGN PROJECT

### 7.3 Appendix 3 - Team Information (All)

Seok Young Choi is a senior at Boston University graduating in Fall 2023. He is pursuing a degree in Computer Engineering (B.S.) and a minor in Mechanical Engineering. Seok Young has interest in computer architecture, digital design, as well as product design and development. While taking computer engineering courses for his major, he discovered his interest in mechanical engineering when he joined the Terrier Motorsports team and acquired knowledge of 3D modeling and mechanical design. Upon completion of his undergraduate studies, he intends to apply his experience and knowledge into practical applications. He can be contacted by email: schoi11@bu.edu, or by phone: 857-361-2236. Nicholas Gutierrez is a senior at Boston University graduating in Spring 2023 with a B.S. degree in Computer Engineering. Prior to attending Boston University, Nicholas had never taken a programming course and found his passion for programming after taking his first class. He has since had two consecutive internships with Amazon Web Services and has completed several personal projects. He has a special interest in algorithmic design and hopes to continue learning after graduation. He can be contacted by email: nickgutz805@gmail.com or by phone: 615-557-3141.
Eunhye Kwon is a senior graduating from Boston University in Spring 2023 with a B.S. in Electrical Engineering. Eunhye has a special interest in control systems, renewable energy, and power distribution. With experience working on control systems at Kulicke and Soffa Inc. and energy distribution at National Grid, Eunhye has a well-rounded understanding of all aspects of electrical systems. Eunhye can be contacted by email: ekwon23@bu.edu, or by phone: 484-682-9222.
Yumin Lisa Wei is a senior at Boston University graduating in Spring of 2023 with a B.S. in Electrical Engineering. Yumin has an interest in circuit design/prototyping, fabrication of integrated circuits, and VLSI. While working at Signify (formerly Phillips Lighting), she learned her love for building prototypes and debugging circuits while also leading a personal project on power savings. There she learned many technical skills required for soldering surface mount and through-hole PCBs. Upon the completion of her undergraduate studies, she intends to apply her knowledge into the semiconductor industry. She can be contacted by email: ylisawei@bu.edu or by phone: 857-222-1758.

### 7.4 Appendix 4 - Controller Prototype (Left Half)

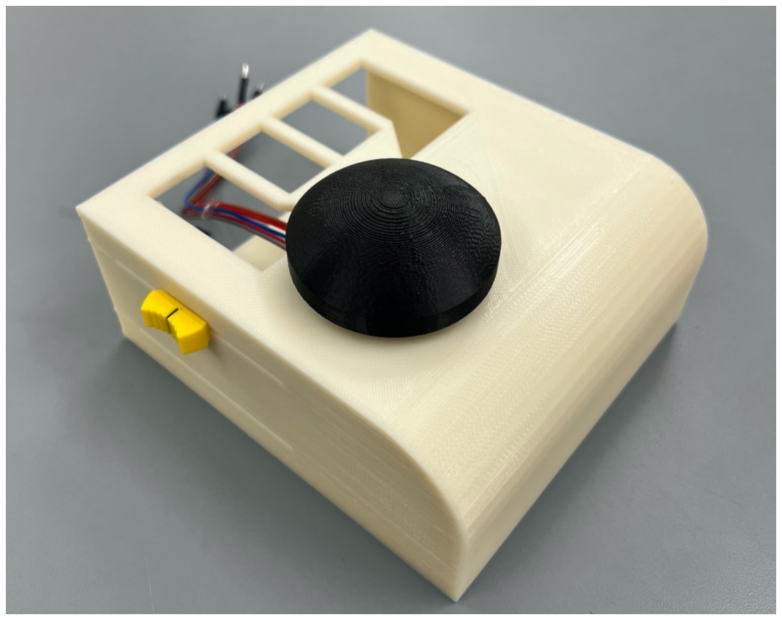
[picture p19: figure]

### 7.5 Appendix 5 - Dimensional Revisions and Feedback (Eunhye and SeokYoung)

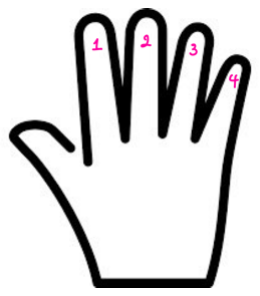
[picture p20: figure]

Button # | Length/Width/Dis-tance from Joystick | Revision: Length/Width/Distance from Joystick | Feedback
Button 1 | 2.50/0.95/0 | 2.50/0.95/0 | • Interchangeable joystick mount sizes to fit user’s hand size • Buttons should be longer/ increase controller width by one or two cen-timeters • Decrease controller height
Button 2 | 1.23/0.7/0.8 | 1.70/0.80/0.8
Button 3 | 1.23/0.7/0.8 | 1.70/0.80/0.8
Button 4 | 2.50/0.7/0 | 2.50/0.90/0

### 7.6 Appendix 6 - Results of Adafruit MPR121 Sensor Material Conductivity Testing (Eunhye)

Material | Conductive? Y/N
Plastic bag | N
Surgical Glove | Y
Cloth | N
Aluminum Metal | Y
3D printer plastic filament | N
Paper | N
Plastic | N
Metal clip | Y

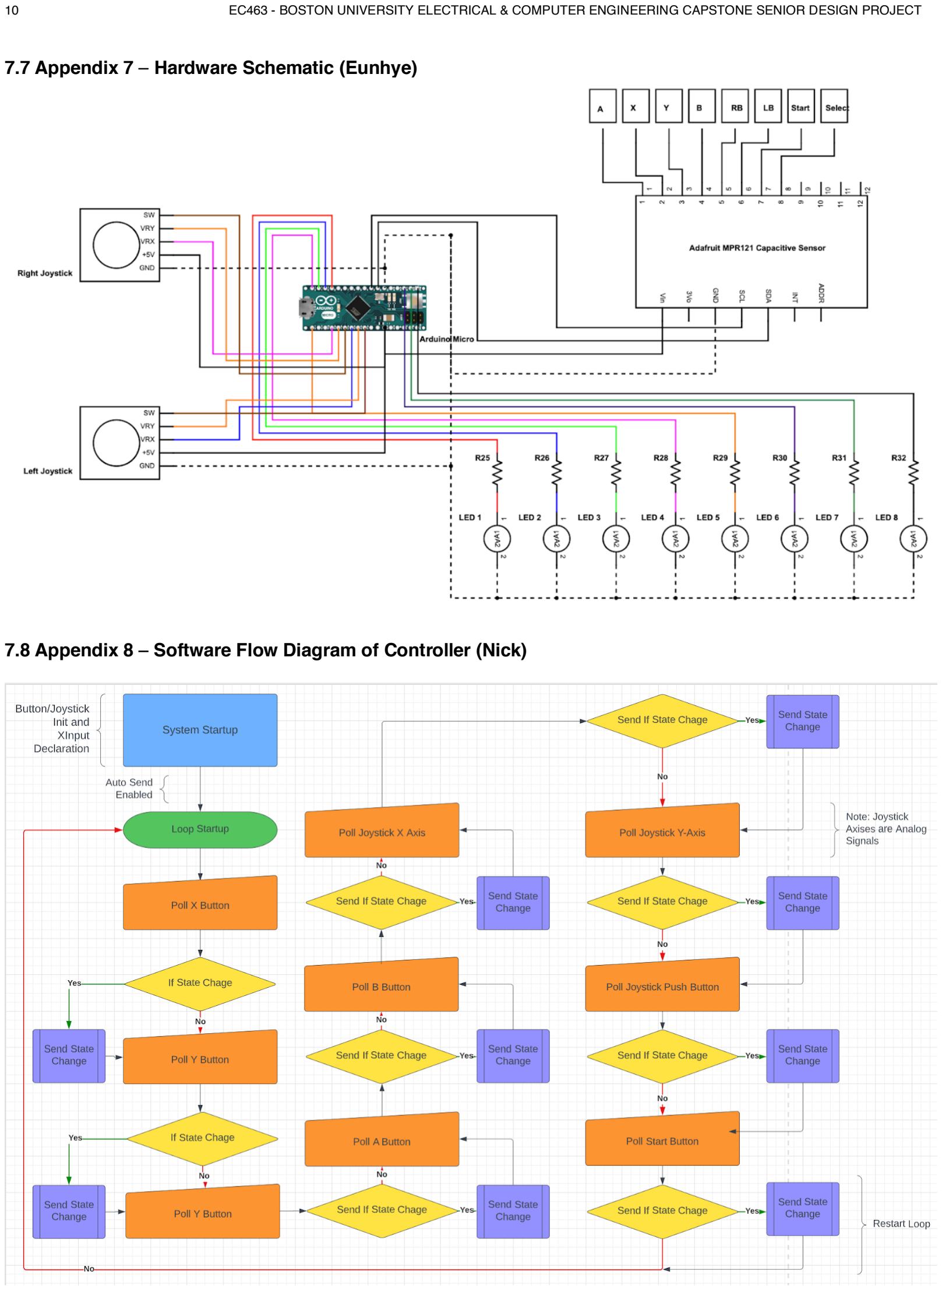
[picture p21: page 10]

10 | EC463 - BOSTON UNIVERSITY ELECTRICAL & COMPUTER ENGINEERING CAPSTONE SENIOR DESIGN PROJECT

### 7.7 Appendix 7 - Hardware Schematic (Eunhye)

### 7.8 Appendix 8 - Software Flow Diagram of Controller (Nick)

7.9 Appendix 9 - Score Sheet of Controller Buttons and Joysticks Testing Result (Nick and Lisa)

Button | Led On/Off? | Correct Controller Output? | Game Action Performed? | Total Score
1 | Yes | Yes | Yes | 100
2 | Yes | Yes | Yes | 100
3 | Yes | Yes | Yes | 100
4 | Yes | Yes | Yes | 100
5 | Yes | Yes | Yes | 100
6 | Yes | Yes | Yes | 100
7 | Yes | Yes | Yes | 100
8 | Yes | Yes | Yes | 100
Left Joystick Push | N/A | Yes | Yes | 100
Right Joystick Push | N/A | Yes | Yes | 100

### 7.10 Appendix 10 - References

[1] Victoria. “'Disabled Gamers' Comprise 20% of Casual-Video Game Audience.” Marketing Charts, June 12, 2008, https://www.marketingcharts.com/industries/media-and-entertainment-4920. [Accessed: October 12, 2022].
[2] “Accessibility in gaming report: Disability charity scope UK,” Scope. [Online]. Available: https://www.scope.org.uk/campaigns/research-policy/accessibility-in-gaming/. [Accessed: October 12, 2022].
[3] “Rheumatoid arthritis,” Mayo Clinic, May 18, 2021. [Online]. Available: https://www.mayoclinic.org/diseases-conditions/rheumatoid-arthritis/symptoms-causes/syc-20353648. [Accessed: October 12, 2022].
[4] “Add video games to your arthritis workout plan,” Living With Arthritis, October 10, 2018. [Online]. Available: http://blog.arthritis.org/living-with-arthritis/video-games-arthritis-workout-plan/. [Accessed: October 12, 2022].
[5 b] “Xbox Adaptive Controller: Xbox,” Xbox.com. [Online]. Available: https://www.xbox.com/en-US/accessories/controllers/xbox-adaptive-controller. [Accessed: October 12, 2022].
[6] “Ask The Application Engineer—35 Capacitance Sensors for Human Interfaces to Electronic Equipment,”Analog, Oct, 2006. [Online]. Available: https://www.analog.com/en/analog-dialogue/articles/capacitance-sensors-for-human-interfaces-to-electronics.html. [Accessed: Dec 5, 2022].

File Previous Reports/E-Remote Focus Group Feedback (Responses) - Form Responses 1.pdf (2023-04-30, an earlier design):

Timestamp

Do you play any video games? How many hours you usually game per week, <1hr, 1-4hrs, 4-8hrs, 8+hrs?
Is it easy to use the

joystick with your palm?

Do you feel any pain or discomfort with your hands in the rest position? (Resting position is when your palms are on the

joysticks and fingers are
in between buttons)

Are the buttons easy for you to reach and press comfortably?

Do you find the placement of the buttons confusing compared to

the standard controller?
(See image above)

If you find the button layout confusing, do you have any suggestions in changing the button

layout?

Do you feel any pain or discomfort when using

the metal buttons on the controller?

Do you find yourself having to move your hand or fingers more

than usual when using
this controller?

Is there any part of the controller that is difficult

to reach or press for you? If so, please specify the part.

Do you feel like the size and shape of the controller are comfortable for your hand?

Do you think you can play games for 30 minutes without experiencing any discomfort or pain in your hands or joints?

Do you believe the e-remote is more comfortable compared to

the standard controller? Is there anything else you would like to add about how the controller feels or works for you?

3/2/2023 17:38:10 1 - 4 hours per week | 5 | 4 | 4 | 1 | 1 | 4
joystick, bc joysticks were too high, it was hard to reach buttons | 5 | 5 | 5
1. joysticks are too high; would feel better pushing down instead of floating; idea - have bottom dented down so bottom of palm can rest 2. peak of sphere is too high
3. cant play without looking; would rather have shorter buttons (in length) and rest position under; maybe some dents at rest position
4. move joysticks closer together 5. slant the top half (where buttons are) down
6. metal flush against plastic 7. more portable
8. logo button is hard to press 9. have hemisphere concaved in 10. rotate casing to have buttons on the down slope
11. add rubber along flat end of joystick 12. closer buttons and more curved button
13. use silly putty to find correct hand position
3/10/2023 9:23:48 I do not play games. | 4 | 3 | 4 | 4
Leave the button placement open because people with RA so they can customize the layout | 2 | 4

joystick and button position, Im using my shoulders too much. I need a hand rest (palm

rest) on the joystick. | 5 | 3 | 3 why does it have to be a capacity button like this? Rumble when you press the button I do not like the new design because my fingers will move with the joystick so the buttons will be hard to press
3/10/2023 9:49:12 I do not play games. | 4 | 4 | 4 | 5 button placement is uncomfortable | 2 | 4

palm rest. Buttons placement is difficult.

joystick size is fine but palm rest would be nice | 4 | 3 | 4

3/10/2023 10:35:28

Less than 1 hour per week | 1 | 4 | 1 | 2
buttons are good, just need to get used to them | 1 | 3 wrist are very uncomfortable | 1 | 2 | 3 Too big for personal preferences Alternate Design: Would be better for wrist pain
3/10/2023 11:09:06 1 - 4 hours per week | 3 | 5 | 4 | 4 a bit a confusing | 4 | 2
get joystick lower so hand is more stretched out | 1 | 2 | 1 Hand pain: across the palm area
3/10/2023 11:14:32 I do not play games. | 5 | 5 | 1 | 1 Button layout needs to be slanted | 1 | 2 joystick hurts palm | 3 | 5 | 1

3/10/2023 11:46:47

Less than 1 hour per week | 1 | 2 | 1 | 2 | 1 | 1 | 1 | 4 | 2
3/10/2023 12:22:35 I do not play games. | 1 | 2 | 2 | 3 no, but I need to get use to them | 1 | 2 no | 1 | 2 | 2
3/10/2023 12:31:50 I do not play games. | 4 | 4 | 5 | 4 Button bothers me a lot | 5 | 5 hand hurts (below index) | 5 | 5 | 5
3/14/2023 13:31:25 1 - 4 hours per week | 2 | 4 | 1 | 2 | 1 | 3

Button placement is a
little confusing and difficult to reach. | 2 | 1 | 1

3/14/2023 13:33:20

Less than 1 hour per week | 4 | 4 | 1 | 4 Placement of button doesn't fit the natural position of my fingers | 1 | 1

index finger and small
finger button was difficult
to reach | 3 | 2 | 1
3/14/2023 13:35:01 1 - 4 hours per week | 1 | 1 | 1 | 1 Would be more comfortable if buttons were slanted | 1 | 1

joystick is too high. If
there is a hand rest on
the joystick, it would be more comfortable to use | 3 | 2 | 2
3/14/2023 13:35:56 1 - 4 hours per week | 4 | 4 | 1 | 1 | 1 | 4 joystick is too high and button placement hurts
| | | | | | the top of my hand | 4 | 4 | 4

3/14/2023 13:36:40

Less than 1 hour per week | 1 | 1 | 1 | 1 | 1 | 1 No, it is very comfortable | 1 | 1 | 1
3/14/2023 13:37:51 I do not play games. | 1 | 1 | 3 | 1

button placement should change to

fit natural curvature of fingers | 1 | 1 Buttons were hard to
reach | 2 | 2 | 2

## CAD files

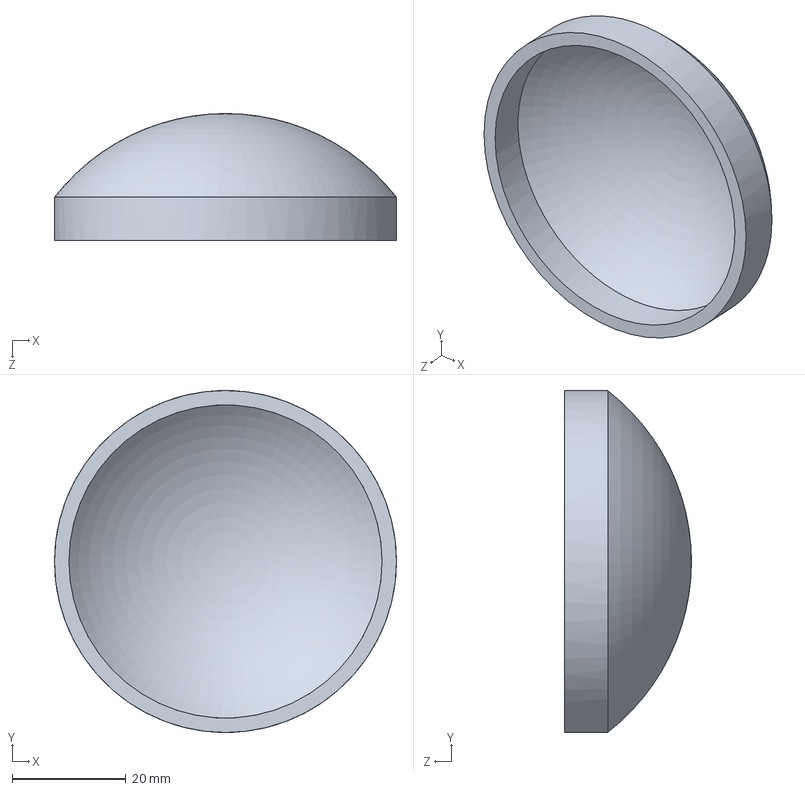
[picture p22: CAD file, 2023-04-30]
Hardware/CAD/joystickLarge.SLDPRT
60.2 x 60.2 x 22.4 mm

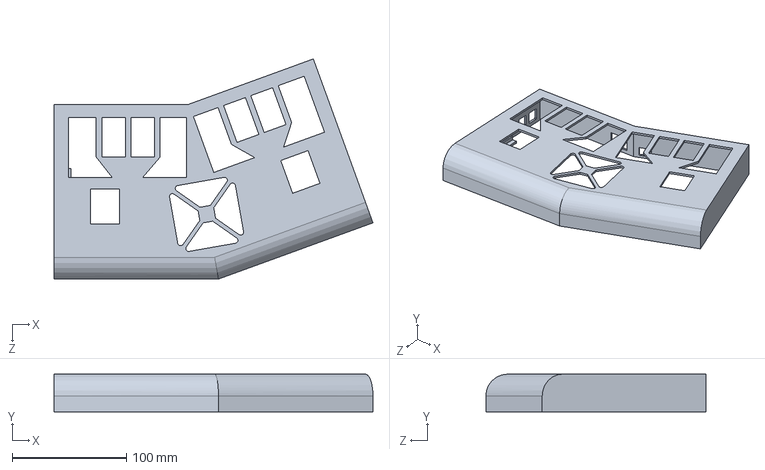
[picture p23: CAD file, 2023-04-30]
Hardware/CAD/casing.SLDPRT
278.8 x 33.0 x 192.4 mm

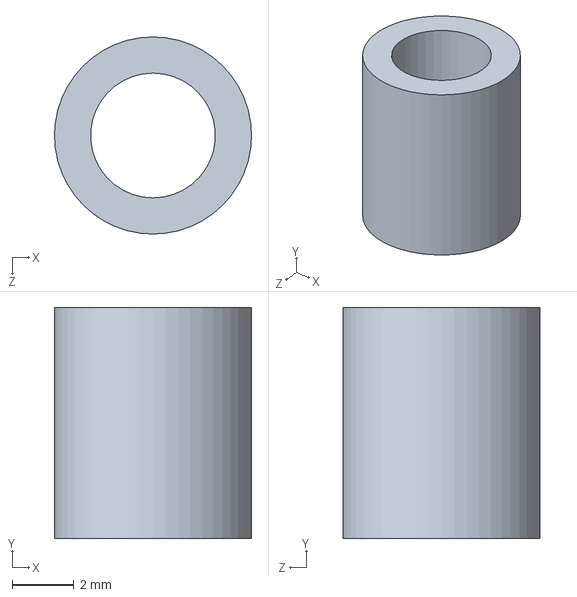
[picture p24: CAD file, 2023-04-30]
Hardware/CAD/connector.SLDPRT
6.40 x 7.50 x 6.40 mm

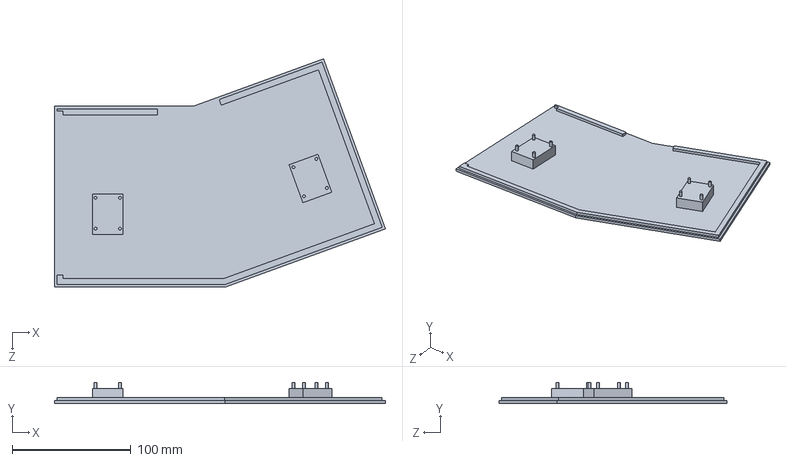
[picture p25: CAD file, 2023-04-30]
Hardware/CAD/base.SLDPRT
278.8 x 17.8 x 192.4 mm

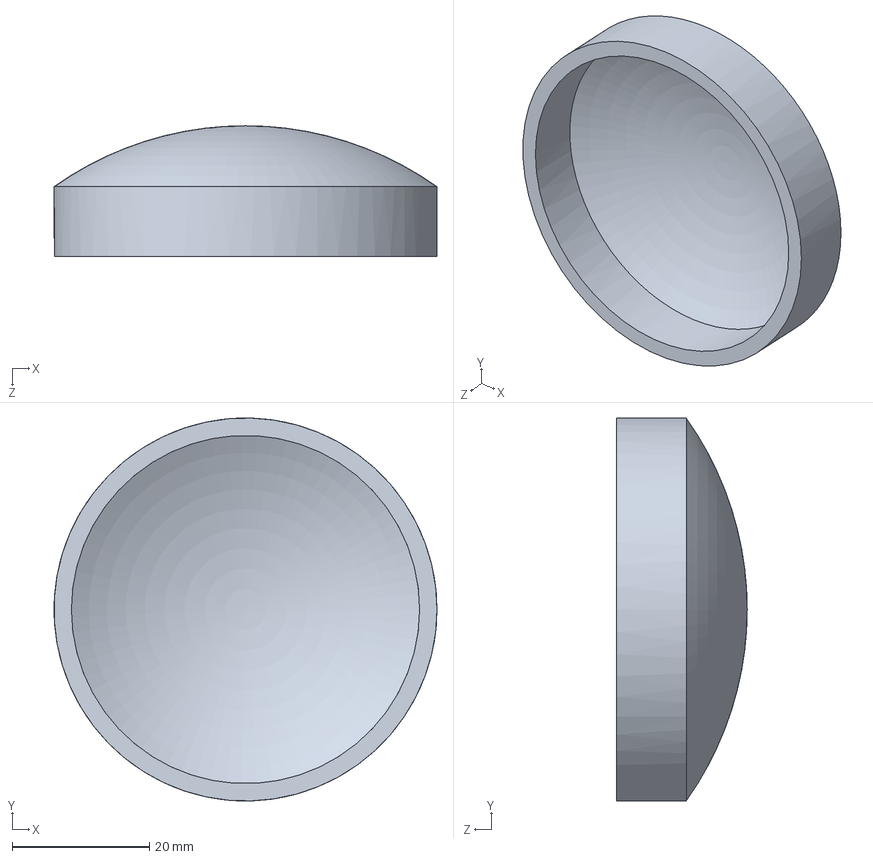
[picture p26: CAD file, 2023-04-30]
Hardware/CAD/joystick.SLDPRT
55.9 x 55.9 x 19.1 mm

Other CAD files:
Hardware/CAD/Buttons.SLDPRT
Hardware/CAD/Dpads.SLDPRT
Hardware/CAD/Buttons.DXF
Hardware/CAD/Dpads.DXF
Hardware/CAD/base.STL
Hardware/CAD/casing.STL
Hardware/CAD/connector.STL
Hardware/CAD/joystick.STL
Hardware/CAD/joystickLarge.STL

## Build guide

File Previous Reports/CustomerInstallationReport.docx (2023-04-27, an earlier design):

Memo

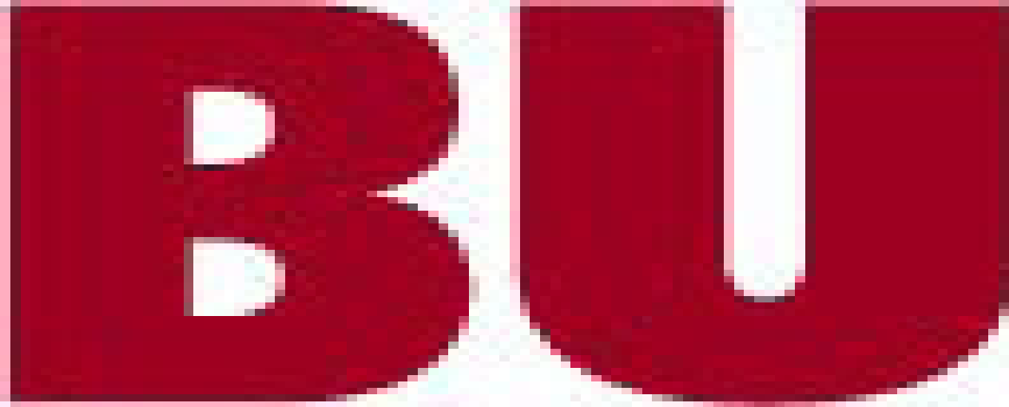
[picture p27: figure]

Senior Design

ENG EC 463

To: Professor Pisano

From: SeokYoung Choi, Nick Gutierrez, Eunhye Kwon, and Yumin Wei

Team: 24

Date: 4/26/2023

Subject: Customer Installation Report

1.0 Detail of Customer Installation

Client: Brandon Miller from Phillips

Location: Phillips Research at 222 Jacobs St., Cambridge, MA 02141

Date of Visit: April 20, 2023

Members Present: SeokYoung Choi, Nick Gutierrez, Eunhye Kwon, Yumin Wei

Customers Present: Brandon Miller and a team of his co-workers

2.0 Requirements

Requirement | Progress
Objective: Create a specialized video game controller for those with hand arthritis to participate in the gaming community more actively | Final Product: E-Remote is an inclusive video game controller for those with hand arthritis.
Function: User-programmable buttons | Final Product: This was completed.
Function: Wireless Bluetooth connectivity with sync time < 30 secs to a PC, PlayStation, or other systems of choice | Final Product: This was completed for a PC.
Function: Intuitive user layout with the basic understanding gained in 5 minutes with provided manual | Final Product: This was completed.
Functions: Reusable batteries to begin → Rechargeable battery source with 3.3V and 24-hour battery life | Final Product: Rechargeable Lithium Ion Polymer Battery (3.7V, 500mAh) and 24-hour runtime
Constraint: Input lag < 200ms | Final Product: Input lag is 100ms.
Constraint: Can fit in a common 22 × 14 × 9 inches backpack | Final Product: 10.7 x 6 x 2.5 inches
Constraint: Cost per Unit < $99.99 | Final Product: The cost of production is $70.50.
Deliverable: A user manual explaining how to configure/operate the controller to the user’s preference and how to connect the controller to their system | Final Product: This was completed.
Deliverable: Demonstration of the overall feasibility of the controller by completing a level from 3 different genres of games (Levels to be chosen together by the design team and client) | Final Product/Exceeded: The E-Remote is compatible with all PC games.

3.0 Overall Assessment

We visited the Philips Research building in Cambridge on April 20 to showcase our final product to our client, Brandon Miller, and his co-workers at Phillips. In a private room, we presented our poster to people in person and online. After the presentation, we answered questions. Some of the questions asked were:

- What was the hardest part about the project? Each problem we came across, we were able to fix, but the one thing we had problems with was figuring out the battery. We decided to use the HUZZAH32 which has a charging port and battery included, but this limited our battery.
- What would be a solution to the battery? Getting a smaller ESP chip and buying our own battery rather than being limited to the HUZZAH board. But this would also require buying a charging port and a charging board.
- What games can you play with the controller? We started with just arcade, puzzle, racing, and shooting, but now with the D-pad, we can play any type of PC game.
- Can you play Mario Kart? Unfortunately, no because we are only compatible with PC, not Nintendo due to proprietary reasons.

After answering questions, we allowed people to choose a game and play with the controller. We continued this demonstration for around an hour, switching between 5 people and 4 games. We also brought the standard Xbox controller, therefore people we able to compete against each other: the E-Remote vs the Xbox controller. From this demo, we received some feedback:

- The left joystick kept popping out, need to fix the joint.
- Input lag was noticeable to one person.

Overall, we believe everything went well. Once we got back to the lab, SeokYoung created new joints and the left joystick is now fixed. Nick also tested the input lag of the E-Remote, and it seems like the problem was because of the projection during the meeting rather than the Bluetooth connectivity.

4.0 Customer Acceptance Email

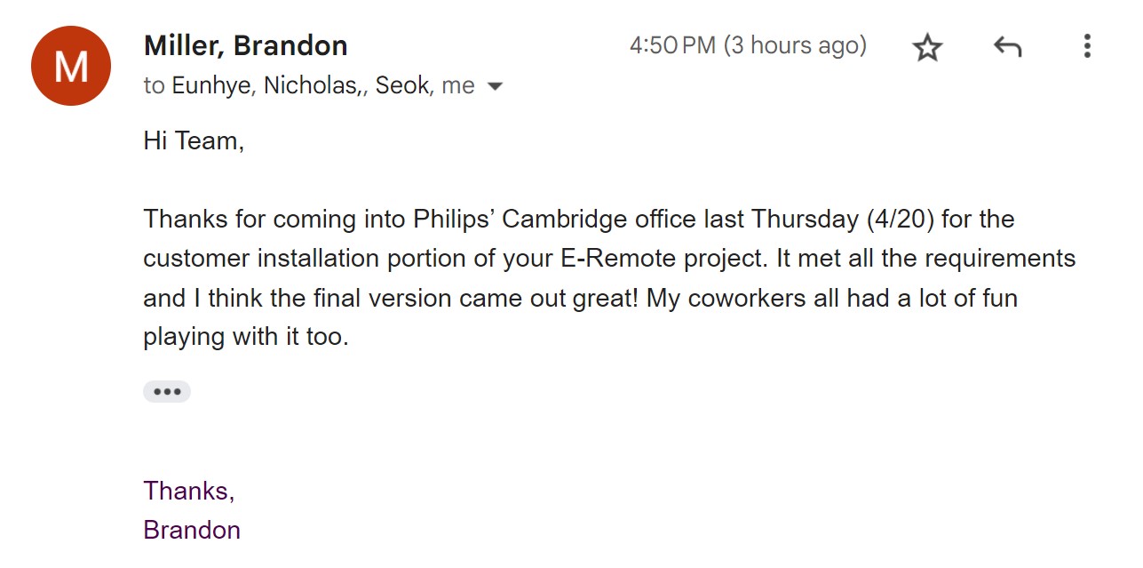
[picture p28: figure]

Figure 1: Customer Acceptance Email from Brandon Miller

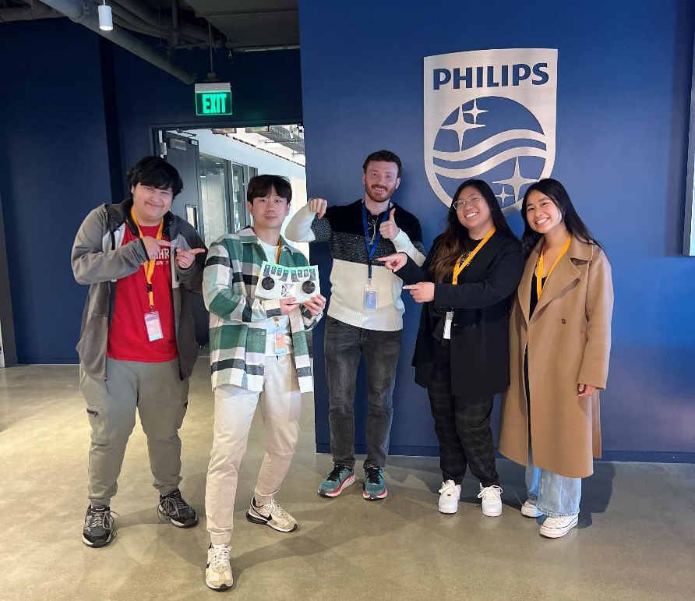
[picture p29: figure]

Figure 2: Team Photo with Brandon Miller at the Phillips Office

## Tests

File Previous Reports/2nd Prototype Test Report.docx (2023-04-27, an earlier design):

Memo


Senior Design

ENG EC 464

To: Professor Pisano

From: Nick Gutierrez, Seok Young Choi, Eunhye Kwon, Lisa Wei

Team: 24

Date: 03/17/2023

Subject: 2nd Prototype Test Report

1.0 Required Materials

Hardware:

- Adafruit HUZZAH32 Esp32 Feather board
- 1 LiPoly battery
- 8 Capacitive Touch Buttons
- Adafruit MPR121 12-Key Capacitive Touch Sensor Breakout
- 3D printed Controller Casing

Software:

- ESP32 code
  - Reads inputs from touch buttons and maps them to controller inputs which are then sent over Bluetooth to the computer.
- Gamepad HTML tester website
  - https://gamepad-tester.com/
- 1 copy of Portal Reloaded to demo in game functionality.

2.0 Setup

1. Power the device by flipping the power switch.
2. Press a couple of buttons to verify inputs are being registered.
3. Open the Gamepad Tester site and verify the controller is being picked up.

3.0 Testing Procedure

1. Demonstrate how the user’s hands should be placed and joystick mobility.
2. Open the Gamepad testing site and demo each button/joystick corresponding to the correct gamepad output.
3. Open Portal Reloaded and show the controller inputs begin the corresponding action in the game
4. Complete the Lasers level of Portal Reloaded

4.0 Measurable Criteria

- Minimal mobility issues when using the palm joysticks and pressing the touch buttons.
- Gamepad testing site shows correct output for controller inputs.
  - Both buttons and joysticks
- Level of Portal Reloaded is demonstrated and completed.

5.0 ESP Input to Controller Button Mapping

Table 1: ESP to Controller Button Mapping

ESP Button | Controller Button
Physical Button 1 (BUTTON_0) | Start
Physical Button 2 (BUTTON_1) | Select
BUTTON_2 | Logo
BUTTON_3 | A
BUTTON_4 | X
BUTTON_5 | LT
BUTTON_6 | LB
BUTTON_7 | RB
BUTTON_8 | RT
BUTTON_9 | A
BUTTON_10 | B

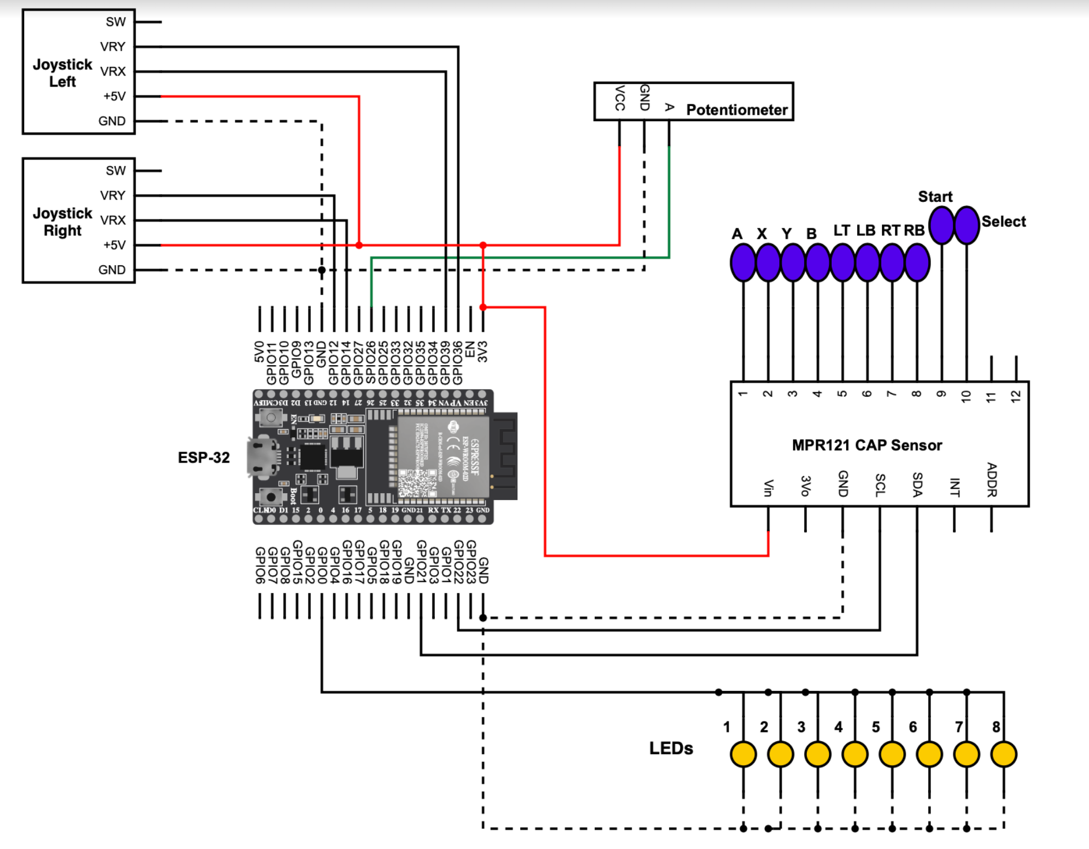
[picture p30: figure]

Fig. 1. Schematic of controller. This controller has an Adafruit HUZZAH32 Esp32 Feather, 8 touch buttons, and two joysticks. Potentiometer and LED lights will be added after further design testing.

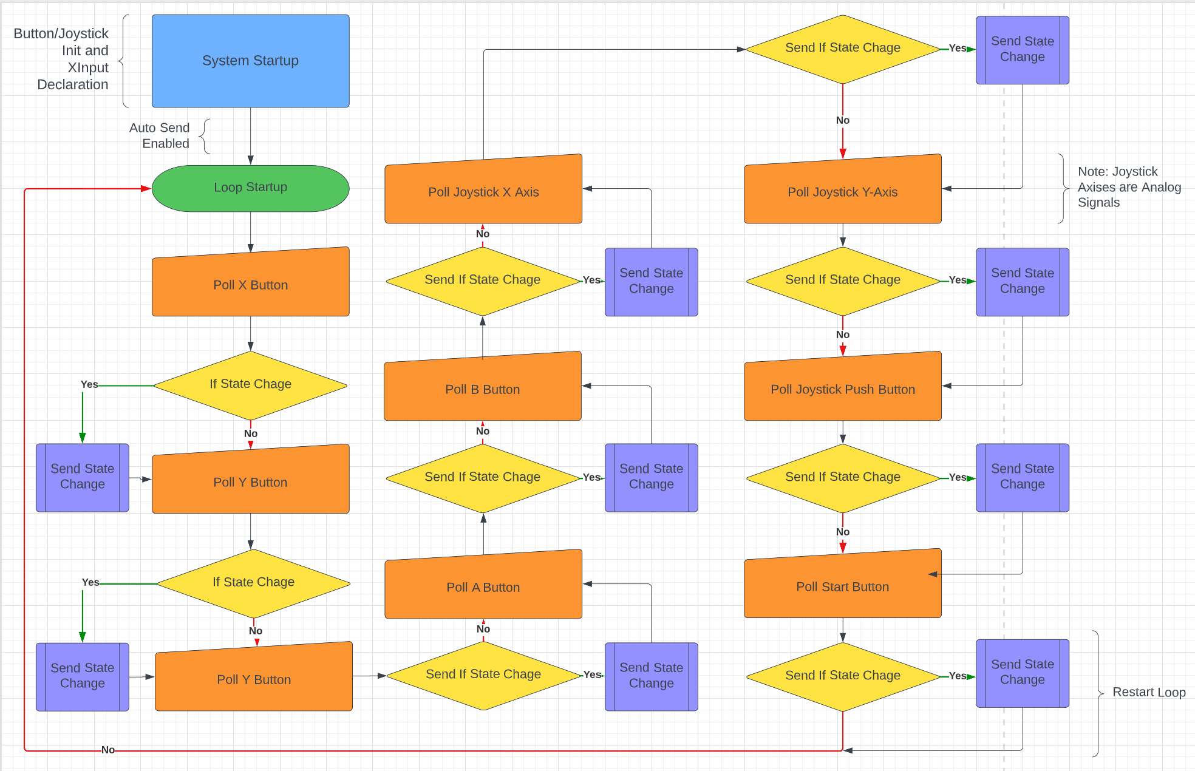
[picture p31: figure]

Fig. 2. Software Flow Diagram of Controller

6.0 Score Sheet

6.1 Controller Hardware/Software Testing

Table 2: Controller buttons and joysticks testing results. The functionality of buttons and joysticks will be tested through LED outputs, gaming controller outputs, and game action performances.

Button | Correct Controller Output? | Game Action Performed? | Button Hard to Press? | Total Score
BUTTON_0 | Yes | Yes | Yes | 60%
BUTTON_1 | Yes | Yes | Yes | 60%
BUTTON_2 | Yes | Yes | No | 100%
BUTTON_3 | Yes | Yes | No | 100%
BUTTON_4 | Yes | Yes | No | 100%
BUTTON_5 | Yes | Yes | No | 100%
BUTTON_6 | Yes | Yes | No | 100%
BUTTON_7 | Yes | Yes | No | 100%
BUTTON_8 | Yes | Yes | No | 100%
BUTTON_9 | Yes | Yes | No | 100%
BUTTON_10 | Yes | Yes | No | 100%

6.2 Boston Medical Center Rheumatology Department Focus Group Test Results

We conducted a focus group study at Boston Medical to assess the usability and effectiveness of our video game controller designed for individuals with hand arthritis. The study included 5 Rheumatologists and 10 patients with hand arthritis who were experiencing difficulties using traditional game controllers.

During the study, participants were asked to perform various tasks using our video game controller, such as navigating through a virtual environment and completing simple gameplay actions. Participants were also asked to provide feedback on the comfort, ease of use, and overall effectiveness of the controller.

The results of the study showed that the majority of participants found the joystick easy to use with their palm. However, 60% of participants reported feeling discomfort when their hands were in the rest position due to the height of the joystick and the placement of the buttons. Many participants reported that the horizontal button placement felt unnatural, and they preferred the buttons to be curved to fit the natural curvature of their fingers. Furthermore, participants noted that the high peak on the joystick was uncomfortable, and they would prefer if the joystick was flatter to enable their hands to be relaxed and stretched out.

On a positive note, 86.6% of participants reported that they did not experience any pain or discomfort when using the touch sensor buttons shown in Fig. 3. The study also revealed mixed responses when participants were asked if they could play games with our video game controller for more than 30 minutes. 53.3% of participants said yes, 13.3% of participants felt uncertain, and 33.3% of participants said no.

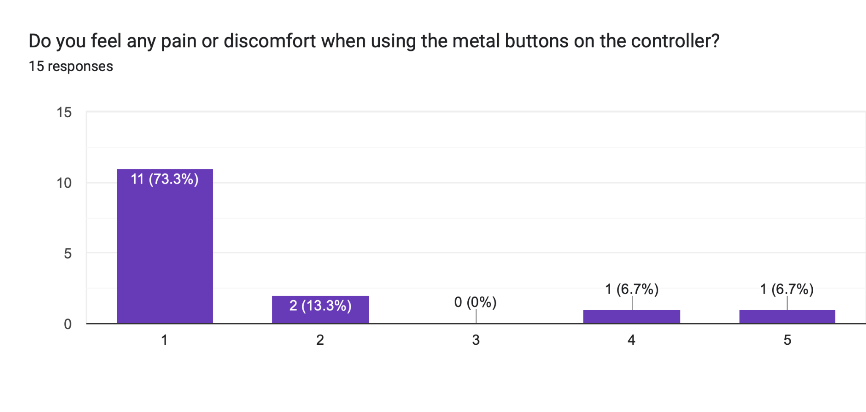
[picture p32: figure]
Forms response chart. Question title: Do you feel any pain or discomfort when using the metal buttons on the controller? . Number of responses: 15 responses.

Fig. 3. Results indicating that the majority of participants did not feel any pain or discomfort when using touch sensor buttons on the controller. Scale of 1-5 with 1 meaning very comfortable and 5 meaning very uncomfortable.

Overall, the Boston Medical focus group test showed that 60% of participants found our video game controller more comfortable than the standard controller. The study also highlighted several areas for improvement, such as adjusting the height and placement of the joystick and buttons to reduce discomfort during extended gameplay sessions.

7.0 Conclusion

After conducting both the prototype test and the Boston Medical focus group test, we have determined that the hardware and software components of the controller are functional and require no further improvements. However, the design of the controller needs more improvement to increase the comfort and usability for individuals with hand arthritis. The results from the focus group test indicated that participants experienced discomfort with the height and placement of the joystick and buttons, which could impact the overall effectiveness of the controller during extended gameplay sessions. The results from the prototype test indicated that two physical buttons were more difficult to press than touch sensor buttons and these might cause discomfort to individuals with hand arthritis. As the next steps of the project, we plan to address these issues by changing the position of the buttons to fit the natural curvature of the fingers and lowering the height of the joystick to ensure that the hand is in a relaxed position. These improvements will be crucial in making the controller more accessible and enjoyable for individuals with hand arthritis.

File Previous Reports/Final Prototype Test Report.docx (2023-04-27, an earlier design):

Memo


Senior Design

ENG EC 463

To: Professor Pisano

From: Nick Gutierrez, Seok Young Choi, Yumin Lisa Wei, Eunhye Kwon

Team: 24

Date: 04/07/23

Subject: Final Prototype Test Report

1.0 Required Materials

Hardware:

- Adafruit HUZZAH32 Esp32 Feather board
- 1 LiPoly battery
- 12 Capacitive Touch Buttons
- 2 Physical Buttons
- Adafruit MPR121 12-Key Capacitive Touch Sensor Breakout
- 3D printed Controller Casing
- 8 Color Cycling LEDs
- 1 Logarithmic Slider
- 1 Power Switch
- 1 Through-hole PCB

Software:

- ESP32 code
  - Reads inputs from touch buttons and maps them to controller inputs which are then sent over Bluetooth to the computer.
- Gamepad HTML tester website
  - https://gamepad-tester.com/
- 1 copy of Marvel’s Spider-Man Remastered to demo in-game functionality.

2.0 Setup

1. Power the device by flipping the power switch.
2. Connect the device to the computer via Bluetooth
3. Press a couple of buttons to verify inputs are being registered.
4. Open the Gamepad Tester site and verify the controller is being picked up.

3.0 Testing Procedure

1. Demonstrate how the user’s hands should be placed and joystick mobility.
2. Demonstrate LED brightness adjustments using the slider
3. Open the Gamepad testing site and demo each button/joystick corresponding to the correct gamepad output.
4. Show control mapping in Steam’s Big Picture Mode
5. Open Spider-Man and show the controller inputs completing the corresponding action in-game
6. Swing around in Spider-Man and demonstrate movement and combat

4.0 Measurable Criteria

- Minimal mobility issues when using the palm joysticks and pressing the touch buttons.
- LED brightness is adjusted with the slider
- Gamepad testing site shows the correct output for controller inputs.
  - Both buttons and joysticks
- Spider-Man is demonstrated and completed.

5.0 Esp Input to Controller Button Mapping

Arduino Button | Controller Button
Physical Button 1 (BUTTON_0) | Start
Physical Button 2 (BUTTON_1) | Select
BUTTON_2 | Left Joystick Push In
BUTTON_3 | Right Joystick Push In
BUTTON_4 | X
BUTTON_5 | Y
BUTTON_6 | LT
BUTTON_7 | LB
BUTTON_8 | RB
BUTTON_9 | RT
BUTTON_10 | A
BUTTON_11 | B
BUTTON_12 | DPad Up
BUTTON_13 | DPad Down
BUTTON_14 | DPad Left
BUTTON_15 | DPad Right

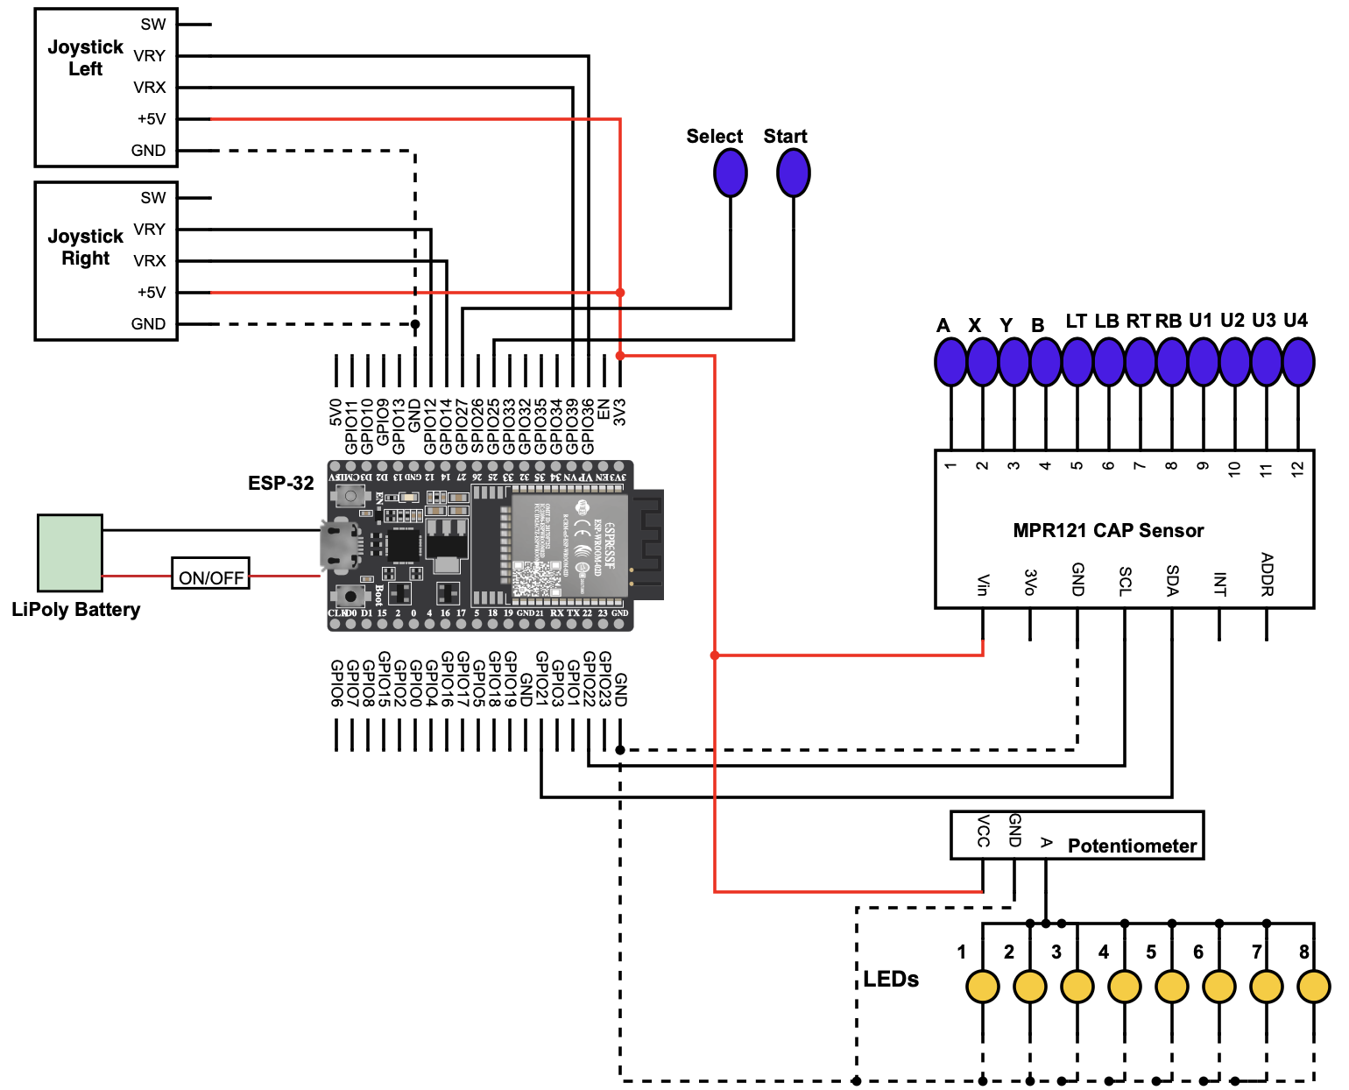
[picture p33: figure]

Figure 1: Schematic of the controller. This controller has an Adafruit HUZZAH32 Esp32 Feather, 12 touch buttons, two physical buttons, a slider, and two joysticks.

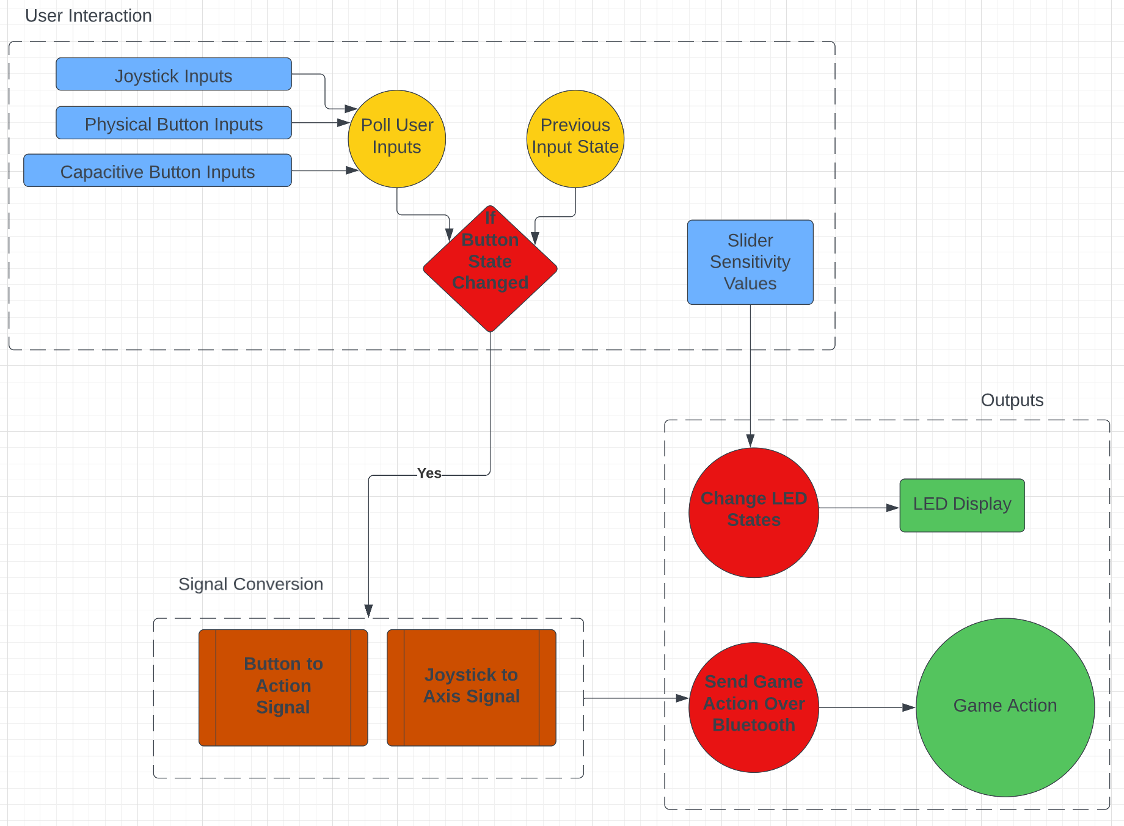
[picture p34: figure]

Figure 2: Software Flow Diagram of Controller. User Inputs are polled in a loop, converted to the proper signals, and sent to the game

6.0 Score Sheet

6.1 Controller Hardware/Software Testing

Table 1: Controller buttons testing results. The functionality of the buttons will be tested through gaming controller outputs, and game action performances.

Button | Correct Controller Output? | Game Action Performed? | Button Hard to Press While Playing? | Total Score
BUTTON_0 | YES | YES | NO | 100%
BUTTON_1 | YES | YES | NO | 100%
BUTTON_2 | YES | YES | NO | 100%
BUTTON_3 | YES | YES | NO | 100%
BUTTON_4 | YES | YES | NO | 100%
BUTTON_5 | YES | YES | NO | 100%
BUTTON_6 | YES | YES | NO | 100%
BUTTON_7 | YES | YES | NO | 100%
BUTTON_8 | YES | YES | NO | 100%
BUTTON_9 | YES | YES | NO | 100%
BUTTON_10 | YES | YES | NO | 100%
BUTTON_11 | YES | YES | NO | 100%
BUTTON_12 | YES | YES | NO | 100%
BUTTON_13 | YES | YES | NO | 100%
BUTTON_14 | YES | YES | NO | 100%
BUTTON_15 | YES | YES | NO | 100%

Table 2: Joystick Testing. The functionality of the joysticks will be tested through gaming controller outputs, game action performances, and ease of use.

Joystick | Comfortable Rest Position? | Easy to Move Around in Game? | Can Be Operated in Tandem with Other Joystick? | Total Score
Left | YES | YES | YES | 100%
Right | YES | YES | YES | 100%

Table 3: Other Hardware. The other pieces of Hardware need to be tested for their individual functionality (defined in the table below) and that they don’t interfere with normal gameplay (blocks buttons, sends mixed signals, etc.).

Hardware | Functioning Properly? | Nonobstructive to Gameplay? | Total Score
Power Switch+Battery (Powers device independent of charging cord) | YES | YES | 100%
LEDs (Light up when the device is powered and cycles through colors) | YES | YES | 100%
Slider (Adjusts LED Brightness) | YES | YES | 100%

7.0 Conclusion

The final prototype of our inclusive video game controller for individuals with hand arthritis has successfully undergone testing for functionality, ease of use, and comfort. Based on feedback from the Boston Medical Center focus group study during our second prototype test, we have made the necessary changes to the prototype and achieved outstanding results.

The controller buttons, joystick, and other hardware components have each received perfect scores for their respective tests. Our team is proud of the progress in developing a product that prioritizes inclusivity and accessibility for individuals with hand arthritis.

Looking towards the future, our team has several planned steps to further improve the functionality and user experience of our inclusive video game controller. Firstly, we will conduct tests on battery life to determine if the lithium-ion polymer battery we have selected can provide 24 hours of continuous gameplay. Additionally, we will perform tests on input lag to ensure that the controller's software can deliver smooth gameplay.

Our team is also looking into incorporating customizable features into the controller design.

Right now, we have interchangeable joystick sizes to allow users to choose the most comfortable joystick size for their hands. We would like to create a more simplified version that is easier for the customer to use.

Moreover, we will make design changes to the controller to enhance its aesthetics and usability. These changes include adding a logo on the side of the controller and incorporating non-slip rubber to the base of the controller to prevent slipping during gameplay.

We are grateful to the Boston Medical Center focus group for providing valuable feedback that enabled us to refine our product to be suitable for individuals with hand arthritis. We are committed to improving our inclusive video game controller to meet the needs and preferences of individuals with hand arthritis. By April 17th, we plan to have a User's Manual available to help users understand and operate our product effectively. Our team is dedicated to creating a product that not only enhances the gaming experience for individuals with hand arthritis but also promotes inclusivity and accessibility in the gaming industry.

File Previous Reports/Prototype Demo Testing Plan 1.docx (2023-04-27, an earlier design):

Memo


Senior Design

ENG EC 463

To: Professor Pisano

From: Nick Gutierrez, Seok Young Choi, Yumin Lisa Wei, Eunhye Kwon

Team: 24

Date: 11/15/22

Subject: Prototype Demo Testing Plan

1.0 Required Materials

Hardware:

- Arduino Micro
- 1 Micro USB to USB A cord
- 8 push buttons
- 8 LEDs of varying colors
- 16 10K Ohm Resistors
- Adafruit MPR121 12-Key Capacitive Touch Sensor Breakout

Software:

- Arduino code
  - Reads inputs from push buttons and maps them to controller inputs which are then sent over USB to the computer
  - Reads push button inputs and lights/unlights corresponding LED
- Gamepad HTML tester website
  - https://gamepad-tester.com/
- 1 copy of Portal Reloaded to demo in game functionality

2.0 Setup

1. Plug in the arduino by connecting the Micro USB to the USB A port on the demo computer
2. If the Gamepad code is not pushed, set the Arduino IDE board to Arduino Micro w/ XInput and push the code
3. Press a couple of buttons to verify inputs are being registered
4. Open the Gamepad Tester site and verify the controller is being picked up

3.0 Testing Procedure

1. Press every button on the device and show every corresponding LED lighting when pressed and unlighting when unpressed
2. Open Gamepad testing site and demo each button/joystick corresponding to the correct gamepad output
3. Open Portal Reloaded and show the controller inputs begin the corresponding action in the game
  a. Joystick Left/Right push will act as Left/Right Trigger so full game actions can be shown
4. Complete the chosen level of Portal Reloaded

4.0 Measurable Criteria

- LEDs light when their corresponding buttons are pressed
- Gamepad testing site shows correct output for controller inputs
  - Both buttons and joysticks
- Level of Portal Reloaded is demonstrated and completed

5.0 Arduino Pinout

Arduino Pin | Output
D9 | LED 1 ON/OFF
D10 | LED 2 ON/OFF
D11 | LED 3 ON/OFF
D12 | LED 4 ON/OFF
D13 | LED 5 ON/OFF
D1 | LED 6 ON/OFF
D17 | LED 7 ON/OFF
D16 | LED 8 ON/OFF

6.0 Arduino Input to Controller Button Mapping

Arduino Button | Controller Button
1 | Start
2 | Select
3 | A
4 | X
5 | Y
6 | B
7 | RB
8 | LB
Joystick Left Push | LT
Joystick Right Push | RT

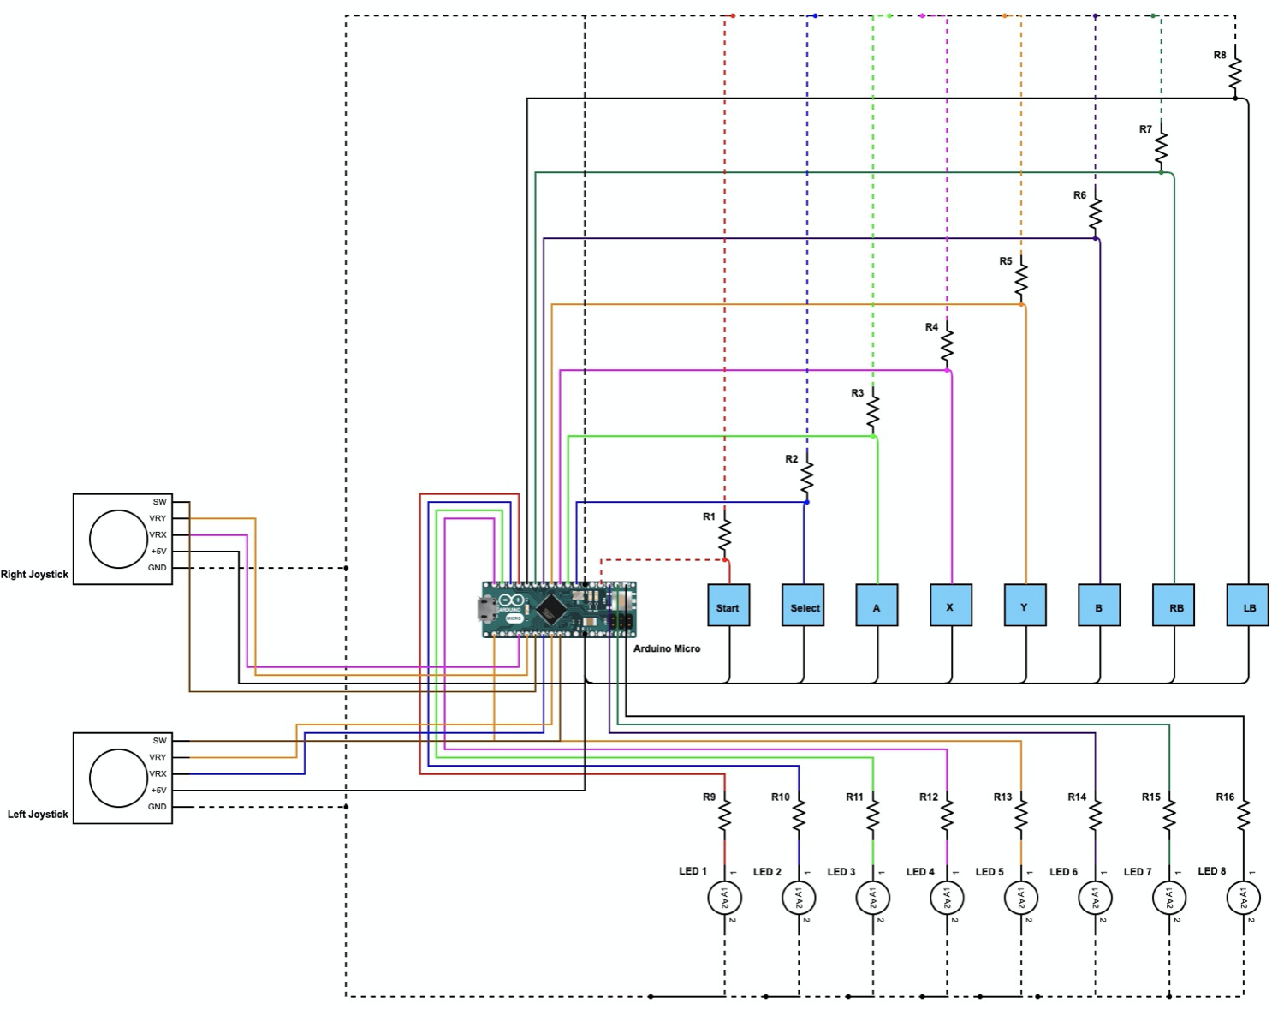
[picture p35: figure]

Figure 1: Schematic of controller. This controller has an Arduino Micro, 8 push buttons, 16 10K ohm resistors, two joysticks, and 8 LED lights.

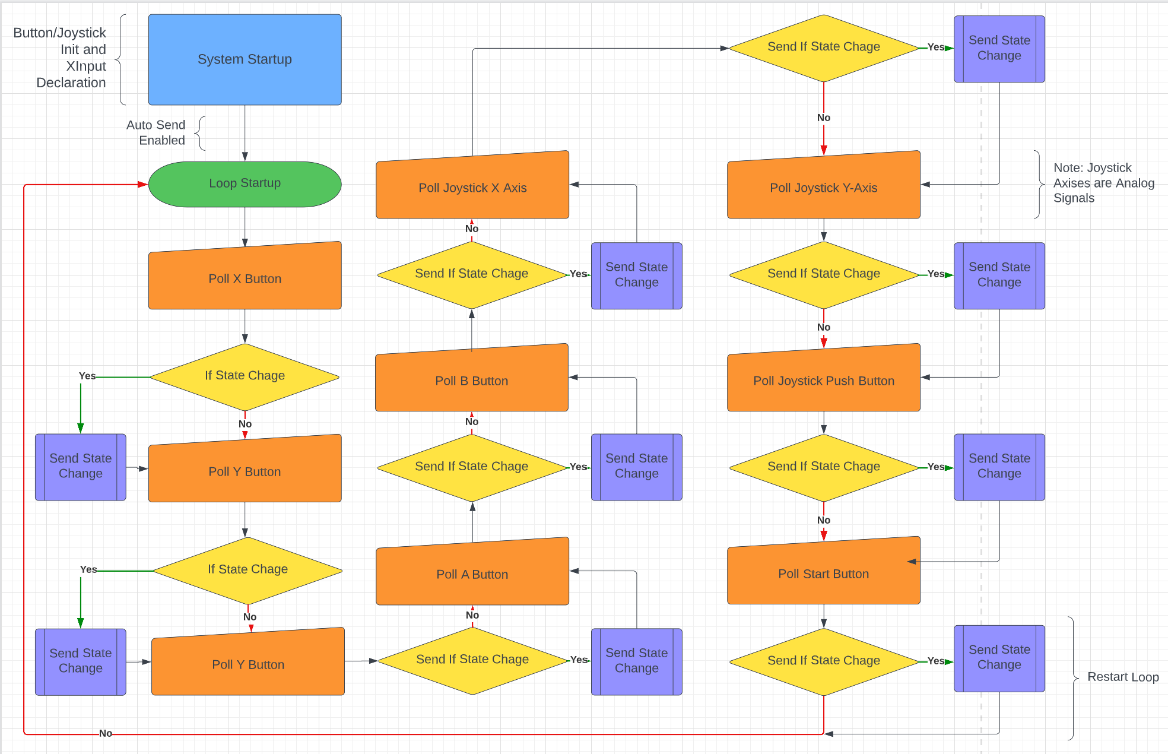
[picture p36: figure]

Figure 2: Software Flow Diagram of Controller

7.0 Score Sheet

7.1 Controller Hardware/Software Testing

Table 1: Controller buttons and joysticks testing results. The functionality of buttons and joysticks will be tested through LED outputs, gaming controller outputs, and game action performances.

Button | Led Lit? | Correct Controller Output? | Game Action Performed? | Total Score
1 | Yes | Yes | Yes | 100
2 | Yes | Yes | Yes | 100
3 | Yes | Yes | Yes | 100
4 | Yes | Yes | Yes | 100
5 | Yes | Yes | Yes | 100
6 | Yes | Yes | Yes | 100
7 | Yes | Yes | Yes | 100
8 | Yes | Yes | Yes | 100
Left Joystick Push | N/A | Yes | Yes | 100
Right Joystick Push | N/A | Yes | Yes | 100

7.2 Capacitive Touch Sensor Testing

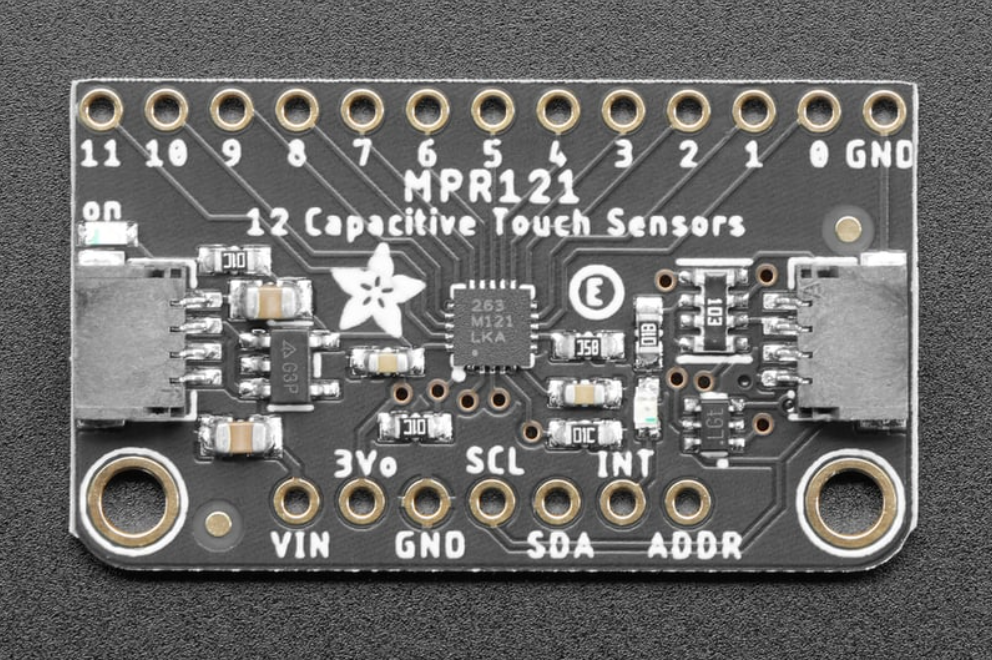
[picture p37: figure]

Figure 1: Adafruit MPR121 12-Key Capacitive Touch Sensor Breakout is used in E-Remote. The MPR121 has 12 sensor pins that will replace push buttons in the initial hardware.

Table 2: Results of Adafruit MPR121 Sensor Material Conductivity Testing. The purpose of this test was to determine the material(s) that could be used as touch sensor pads of E-Remote.

Material | Conductive? Y/N
Plastic bag | N
Surgical Glove | Y
Cloth | N
Aluminum Metal | Y
3D printer plastic filament | N
Paper | N
Plastic | N
Metal clip | Y

It is concluded that we need a conductive material for the touch sensor pads. Aluminum or steel metal sheets would work best for our design. The metal sheet would have laser cut holes so that LED light can shine through. The metal sensor would be protected with a conductive plastic film.

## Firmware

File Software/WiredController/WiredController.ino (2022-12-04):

#include <XInput.h>
#include <Wire.h>
#include "Adafruit_MPR121.h"

#ifndef _BV
#define _BV(bit) (1 << (bit)) 
#endif

const int LeftJoyXPin = A3;
const int LeftJoyYPin = A4;
const int LeftJoyPushPin = 15;

const int RightJoyXPin = A0;
const int RightJoyYPin = A1;
const int RightJoyPushPin = A5;

const int led1 = 9;
const int led2 = 10;
const int led3 = 11;
const int led4 = 12;
const int led5 = 13;
const int led6 = 1;
const int led7 = 17;
const int led8 = 16;

int touchInputs[8] = {0,0,0,0,0,0,0,0};

uint16_t currtouched = 0;
Adafruit_MPR121 cap = Adafruit_MPR121();

void setup() {
  pinMode(LED_BUILTIN, OUTPUT);
  pinMode(led1, OUTPUT);
  pinMode(led2, OUTPUT);
  pinMode(led3, OUTPUT);
  pinMode(led4, OUTPUT);
  pinMode(led5, OUTPUT);
  pinMode(led6, OUTPUT);
  pinMode(led7, OUTPUT);
  pinMode(led8, OUTPUT);

  while(!cap.begin(0x5A)){
    digitalWrite(LED_BUILTIN, 1);
  }

  digitalWrite(LED_BUILTIN, 0); 

  XInput.begin();
}

void loop() {
  currtouched = cap.touched();
  boolean LeftJoyPushState = currtouched & _BV(0);
  for(uint8_t i = 0;i < 12;i++){
    touchInputs[i] = currtouched & _BV(i);
  }
  
  boolean StartState = touchInputs[0];
	XInput.setButton(BUTTON_A, StartState);   // press Start conditionally
  digitalWrite(led1, StartState);

  boolean SelectState = touchInputs[1];
	XInput.setButton(BUTTON_X, SelectState);   // press Select conditionally
  digitalWrite(led2, SelectState);

	boolean AState = touchInputs[2];
	XInput.setButton(BUTTON_B, AState);   // press A conditionally
  digitalWrite(led3, AState);

  boolean XState = touchInputs[3];
	XInput.setButton(BUTTON_Y, XState);   // press X conditionally
  digitalWrite(led4, XState);

  boolean YState = touchInputs[4];
	XInput.setButton(DPAD_UP, YState);   // press Y conditionally
  digitalWrite(led5, YState);

  boolean BState = touchInputs[5];
	XInput.setButton(DPAD_DOWN, BState);   // press B conditionally
  digitalWrite(led6, BState);

  boolean RBState = touchInputs[6];
	XInput.setButton(DPAD_LEFT, RBState);   // press RB conditionally
  digitalWrite(led7, RBState);

  boolean LBState = touchInputs[7];
	XInput.setButton(DPAD_RIGHT, LBState);   // press LB conditionally
  digitalWrite(led8, LBState);

  XInput.setRange(JOY_LEFT, 0, 1023);  // using analogRead (10-bit ADC)
  XInput.setRange(JOY_RIGHT, 0, 1023);  // using analogRead (10-bit ADC)
  pinMode(LeftJoyPushPin, INPUT_PULLUP);
  pinMode(RightJoyPushPin, INPUT_PULLUP);

  int LeftJoyXState = analogRead(LeftJoyXPin);
  int LeftJoyYState = analogRead(LeftJoyYPin);
  XInput.setJoystickX(JOY_LEFT, LeftJoyYState, true);
  XInput.setJoystickY(JOY_LEFT, LeftJoyXState, true); //Y axis needed to be inverted for correct positioning

  boolean LeftJoyPushState = !digitalRead(LeftJoyPushPin);
  XInput.setButton(TRIGGER_LEFT, LeftJoyPushState);   // press L3 Right conditionally

  int RightJoyXState = analogRead(RightJoyXPin);
  int RightJoyYState = analogRead(RightJoyYPin);
  XInput.setJoystickX(JOY_RIGHT, RightJoyXState, false);
  XInput.setJoystickY(JOY_RIGHT, RightJoyYState, true); //Y axis needed to be inverted for correct positioning

  boolean RightJoyPushState = !digitalRead(RightJoyPushPin);
  XInput.setButton(TRIGGER_RIGHT, RightJoyPushState);   // press L3 Right conditionally
}

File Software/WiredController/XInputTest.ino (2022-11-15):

#include <XInput.h>

const int StartButtonPin = 0;
const int SelectButtonPin = 2;

const int AButtonPin = 3;
const int XButtonPin = 4;
const int YButtonPin = 5;
const int BButtonPin = 6;

const int RBButtonPin = 7;
const int LBButtonPin = 8;

const int LeftJoyXPin = A3;
const int LeftJoyYPin = A4;
const int LeftJoyPushPin = 15;

const int RightJoyXPin = A0;
const int RightJoyYPin = A1;
const int RightJoyPushPin = A5;

const int led1 = 9;
const int led2 = 10;
const int led3 = 11;
const int led4 = 12;
const int led5 = 13;
const int led6 = 1;
const int led7 = 17;
const int led8 = 16;

void setup() {
  pinMode(led1, OUTPUT);
  pinMode(led2, OUTPUT);
  pinMode(led3, OUTPUT);
  pinMode(led4, OUTPUT);
  pinMode(led5, OUTPUT);
  pinMode(led6, OUTPUT);
  pinMode(led7, OUTPUT);
  pinMode(led8, OUTPUT);
  
  pinMode(StartButtonPin, INPUT_PULLUP);
  pinMode(SelectButtonPin, INPUT_PULLUP);

  pinMode(AButtonPin, INPUT_PULLUP);
  pinMode(XButtonPin, INPUT_PULLUP);
  pinMode(YButtonPin, INPUT_PULLUP);
  pinMode(BButtonPin, INPUT_PULLUP);

  pinMode(RBButtonPin, INPUT_PULLUP);
  pinMode(LBButtonPin, INPUT_PULLUP);

  XInput.setRange(JOY_LEFT, 0, 1023);  // using analogRead (10-bit ADC)
  XInput.setRange(JOY_RIGHT, 0, 1023);  // using analogRead (10-bit ADC)
  pinMode(LeftJoyPushPin, INPUT_PULLUP);
  pinMode(RightJoyPushPin, INPUT_PULLUP);
	
  XInput.begin();
}

void loop() {
  boolean StartState = digitalRead(StartButtonPin);
	XInput.setButton(BUTTON_START, StartState);   // press Start conditionally
  digitalWrite(led1, StartState);

  boolean SelectState = digitalRead(SelectButtonPin);
	XInput.setButton(BUTTON_BACK, SelectState);   // press Select conditionally
  digitalWrite(led2, SelectState);

	boolean AState = digitalRead(AButtonPin);
	XInput.setButton(BUTTON_A, AState);   // press A conditionally
  digitalWrite(led3, AState);

  boolean XState = digitalRead(XButtonPin);
	XInput.setButton(BUTTON_X, XState);   // press X conditionally
  digitalWrite(led4, XState);

  boolean YState = digitalRead(YButtonPin);
	XInput.setButton(BUTTON_Y, YState);   // press Y conditionally
  digitalWrite(led5, YState);

  boolean BState = digitalRead(BButtonPin);
	XInput.setButton(BUTTON_B, BState);   // press B conditionally
  digitalWrite(led6, BState);

  boolean RBState = digitalRead(RBButtonPin);
	XInput.setButton(BUTTON_RB, RBState);   // press RB conditionally
  digitalWrite(led7, RBState);

  boolean LBState = digitalRead(LBButtonPin);
	XInput.setButton(BUTTON_LB, LBState);   // press LB conditionally
  digitalWrite(led8, LBState);

  int LeftJoyXState = analogRead(LeftJoyXPin);
  int LeftJoyYState = analogRead(LeftJoyYPin);
  XInput.setJoystickX(JOY_LEFT, LeftJoyXState, false);
  XInput.setJoystickY(JOY_LEFT, LeftJoyYState, true); //Y axis needed to be inverted for correct positioning

  boolean LeftJoyPushState = !digitalRead(LeftJoyPushPin);
  XInput.setButton(TRIGGER_LEFT, LeftJoyPushState);   // press L3 Right conditionally

  int RightJoyXState = analogRead(RightJoyXPin);
  int RightJoyYState = analogRead(RightJoyYPin);
  XInput.setJoystickX(JOY_RIGHT, RightJoyXState, false);
  XInput.setJoystickY(JOY_RIGHT, RightJoyYState, true); //Y axis needed to be inverted for correct positioning

  boolean RightJoyPushState = !digitalRead(RightJoyPushPin);
  XInput.setButton(TRIGGER_RIGHT, RightJoyPushState);   // press L3 Right conditionally
}

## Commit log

2022-11-02 Add files via upload
    Schematic of Controller with 8 buttons, 8 LEDs, and 2Joysticks
2022-11-17 V1 Controller with Capacitive Button Inputs
2022-12-04 Create WiredController
2022-12-12 Create WirelessController
2023-01-27 2 Working Joysticks,4 Capacitive,6 Digital Button
2023-02-09 Read Baseline and Filtered Data
2023-02-09 Slider for Color Shift LEDs
2023-02-14 Capacitive Touch Update
2023-02-16 Migrated to Adafruit Huzzah Feather board
2023-02-19 Potential read and report battery level
2023-02-23 Removed Battery Level Report
2023-03-02 Second Prototype Code
2023-03-27 Wokring Version that filters Drift
2023-03-30 Final Prototype Working Version A
2023-04-18 Version C: Drift Fix No Hard Coding
    Fixed Drift for both battery and wired without hard coding
2023-04-30 Hardware README and Front Page README
    [Buttons.DXF, Buttons.SLDPRT, Dpads.DXF, Dpads.SLDPRT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]
